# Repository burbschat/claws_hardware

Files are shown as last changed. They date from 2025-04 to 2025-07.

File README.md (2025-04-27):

# Simple SiPM/plastic scintillator based beam loss monitors
## Introduction
This repository contains the hardware design for a kind of SiPM/plastic
scintillator based beam loss monitor.
The design is based on and borrows the name (*CLAWS*) from an earlier design
employed during commissioning of the SuperKEKB collider.
A related thesis can be found [here](https://mediatum.ub.tum.de/1624845).
CLAWS was supposed to be a abbreviation for some longer name but it surely
wasn't a very elegant one, neither can I seem to remember it. Anyhow, as a
short name is quite practical, we kept on calling the system *CLAWS*.

The sensors later have been re-purposed to detect beam loss and trigger a beam
abort if there is too much of it. This application does not require very
precise sensors. Further, opposed to the original design, now a larger dynamic
range was desirable. To also allow for measurement of beam backgrounds
which occur for longer than a few microseconds, DC coupled analog electronics
are required.
The design published here was created to implement the required changes
outlined above and create a system better suited to the current application at
the SuperKEKB collider.

## Disclaimer
The circuits here have been designed by an at the time undergrad student (me)
who had no real experience in electronics or electronics CAD. I am sure there
are many aspects that I would do differently now, be it related to the circuit
itself or how it is described in KiCad.
I am however of course open for suggestions to improve the design (although I
cannot guarantee I will find the time to implement them myself).

## Overview
There are two parts to the detector system: The detectors, which are to be
placed where the beam background is expected to occur and the receiver board,
which should be placed near the digitizer, which is usually positioned outside
the radiation controlled area of the accelerator complex.

The following is an illustration of the use case at SuperKEKB (use for beam
abort), also illustrating the detector structure.
We employ a special trigger to reject short background spikes. The analog
signal however can be used in any other conceivable way depending on the exact
application.

illustration of use at SuperKEKB

### Detector Board
The detector (sometimes also referred to as the sensor) is based on a plastic
scintillator (BC-408 or similar material), light from which is detected using a
Hamamatsu SiPM (or MPPC). The SiPM is located in a small dimple in the bottom
of the scintillator. The scintillator is wrapped in an appropriately sized
reflective film (M3 DF2000MA or similar) to make sure as much as possible light
reaches the SiPM. This is the same as what was used with the earlier versions
of CLAWS and can be traced back to what is described in [this paper](https://arxiv.org/abs/1512.05900).
The wrapped scintillator is fixed to the PCB using black aluminium tape, which
also serves to shut out any light from the environment, which would overwhelm
(and potentially damage) the SiPM.

The signal obtained from the SiPM is turned into a differential signal using
the LMH6553 fully differential amplifier. The gain of this amplifier may be set
by choosing appropriate resistor values in the feedback loops of the circuit.
This amplifier then drives a differential pair in an ordinary Ethernet cable.
However, generally only CAT6A or CAT7 cables are used, as they usually provide
superior shielding, which even though a differential pair is used, appeared to
significantly lower the noise introduced by the cable.

The required voltages to drive the amplifier circuit as well as the SiPM bias
voltage are obtained from the same Ethernet cable. The amplifier here is
configured with a single 10V power supply. The voltage in the cable should be
slightly above 10V, as it is regulated by a LDO regulator on the detector
board.
10V is the maximum supply voltage supported by the LMH6553 and is chosen to
maximize the dynamic range at the amplifier output (which depends on the supply
voltage).

One twisted pair in the cable remains unused for now.

detector board V4.1

### Receiver Board
The differential signal provided by the detector board is received and properly
terminated by the receiver board. It contains a circuit using the same LMH6553
fully differential amplifier, which provides further amplification of the
received signal, as well as the option to convert it to a single ended signal.
Both inverted and non-inverted signals are supported. The not used side must be
terminated using a 50Ohm resistor (which can however also be mounted directly
on the board while leaving the corresponding output connector unpopulated).
There also is the option to further use both outputs at the same time to obtain
a differential signal.

The receiver amplifier circuit is, opposed to the one on the detector board,
arranged in a symmetric configuration. This is done to avoid a large DC bias at
the output, which poses no problem for in case of the detector board, as it is
removed by the receiver amplification circuit. The symmetric configuration
necessitates +5V and -5V supplies (for both of which there are LDO regulators
on the board).

Presumably due some unavoidable variations in the used components (resistance
values etc.), the circuit is never perfectly symmetric and thus a small DC bias
remains. The same bias appears at both outputs (inverted and non-inverted).
To compensate this, the common mode output voltage control pin of the LMH6553
is used, which is accessible through a potentiometer on the board.
As the bias is present at both outputs, one can only ever tune the circuit to
have one of them centered perfectly around zero. This however should pose no
significant problem, as in most use cases one probably only uses one of the two
outputs, or uses both to get a differential signal, for which a small DC bias
does not matter.

receiver board

The Receiver board further also distributes the voltages required by the
detector boards. These voltages as well as those needed by the receiver board
itself are supplied externally through connectors on the side of the board.
There further is the option to daisy-chain multiple receiver boards and share
the supply voltages between them. Which voltage should be connected to what is
to some degree configurable using a set of jumper pins. As regulators are used
for all but the SiPM bias voltage, the low voltages provided can be chosen
rather freely, as long as they fall within the ranges supported input of the
LDO regulators. However, testing showed that if they are on the high side, the
LDOs get rather hot. Whether this is still within the supported temperature
range was not (yet) verified.

There is also an option to use the positive voltage (before the LDO) for the
receiver board amplifier as the positive voltage for the detector board
amplifier. This turned out to be the most convenient configuration as it allows 
the setup to be powered off a +/-12V double rail supply (next to a supply for
the SiPM bias voltage).

To share voltages between receiver boards, a 10-pin ribbon cable is used. The
boards may be arranged in a stacked configuration, in case of which the
connector on the bottom must be installed and used, or a flat configuration
with a single long ribbon cable with multiple connectors.

A example for the stacked configuration is shown below. There is theoretically
also the option to add further boards of the same form factor which for example
may contain a high voltage power supply to provide the SiPM bias voltage, or
DC/DC converters to provide the other supply voltages. A mockup is shown in the
figure below.

receiver boards tower configuration

### SiPM Bias Voltage Supply
To avoid having to prepare a adjustable power supply supporting up to ~60V for
every setup, it was attempted to design a simple circuit based on the LT3571
75V DC/DC Converter for APD Bias.
The design appears to function alright, but does not provide a very flat voltage.
This to some extend is reflected in the signal form the SiPM. However, for the
application at SuperKEKB, the signal does not have to be very precise and the
introduced noise can be tolerated.

The board also does indeed emit some EMI, so care must be taken on where to
position it. There likely are possibilities to improve this design. I am open
for suggestions.

The board can be run off the same +12V as used as an input to the receiver
board. There is the option to use a DAC in combination with a microcontroller
to set the voltages and possibly read them back. I did not yet get around to
prepare a proper firmware for that. One can also simply adjust the voltage 
using a potentiometer.

There are four channels on one board, just because four of them appeared to
fit. One can just not populate the unused ones, if less than four are required.
The board does not support the same interconnect headers as the receiver boards.
This is because it mainly was designed to see if the circuit does work/is
usable at all. One could create a new version with only one channel featuring
the interconnect header.

## KiCad
The design is entirely drawn in KiCad. I like to use the newest version. The
files in this repository are for version 9.

## Libraries
There is are custom symbol and footprint library containing all the parts not
present in the standard KiCad libraries. The provided 3D models are managed
with git LFS.

## Simulation
Some of the symbols reference SPICE models in the `${KIPRJMOD}/../lib/spice_models/` directory.
Those are not present in this repository as I am probably not permitted to distribute them.
If simulation is required, please acquire the models directly from the manufacturers.

## KiBot
KiBot can be used to automate creation of gerber files, export circuit diagrams
and assembly documents or similar. The included configs are those which I used
when producing the boards at use for the SuperKEKB abort system. Adjust to taste.

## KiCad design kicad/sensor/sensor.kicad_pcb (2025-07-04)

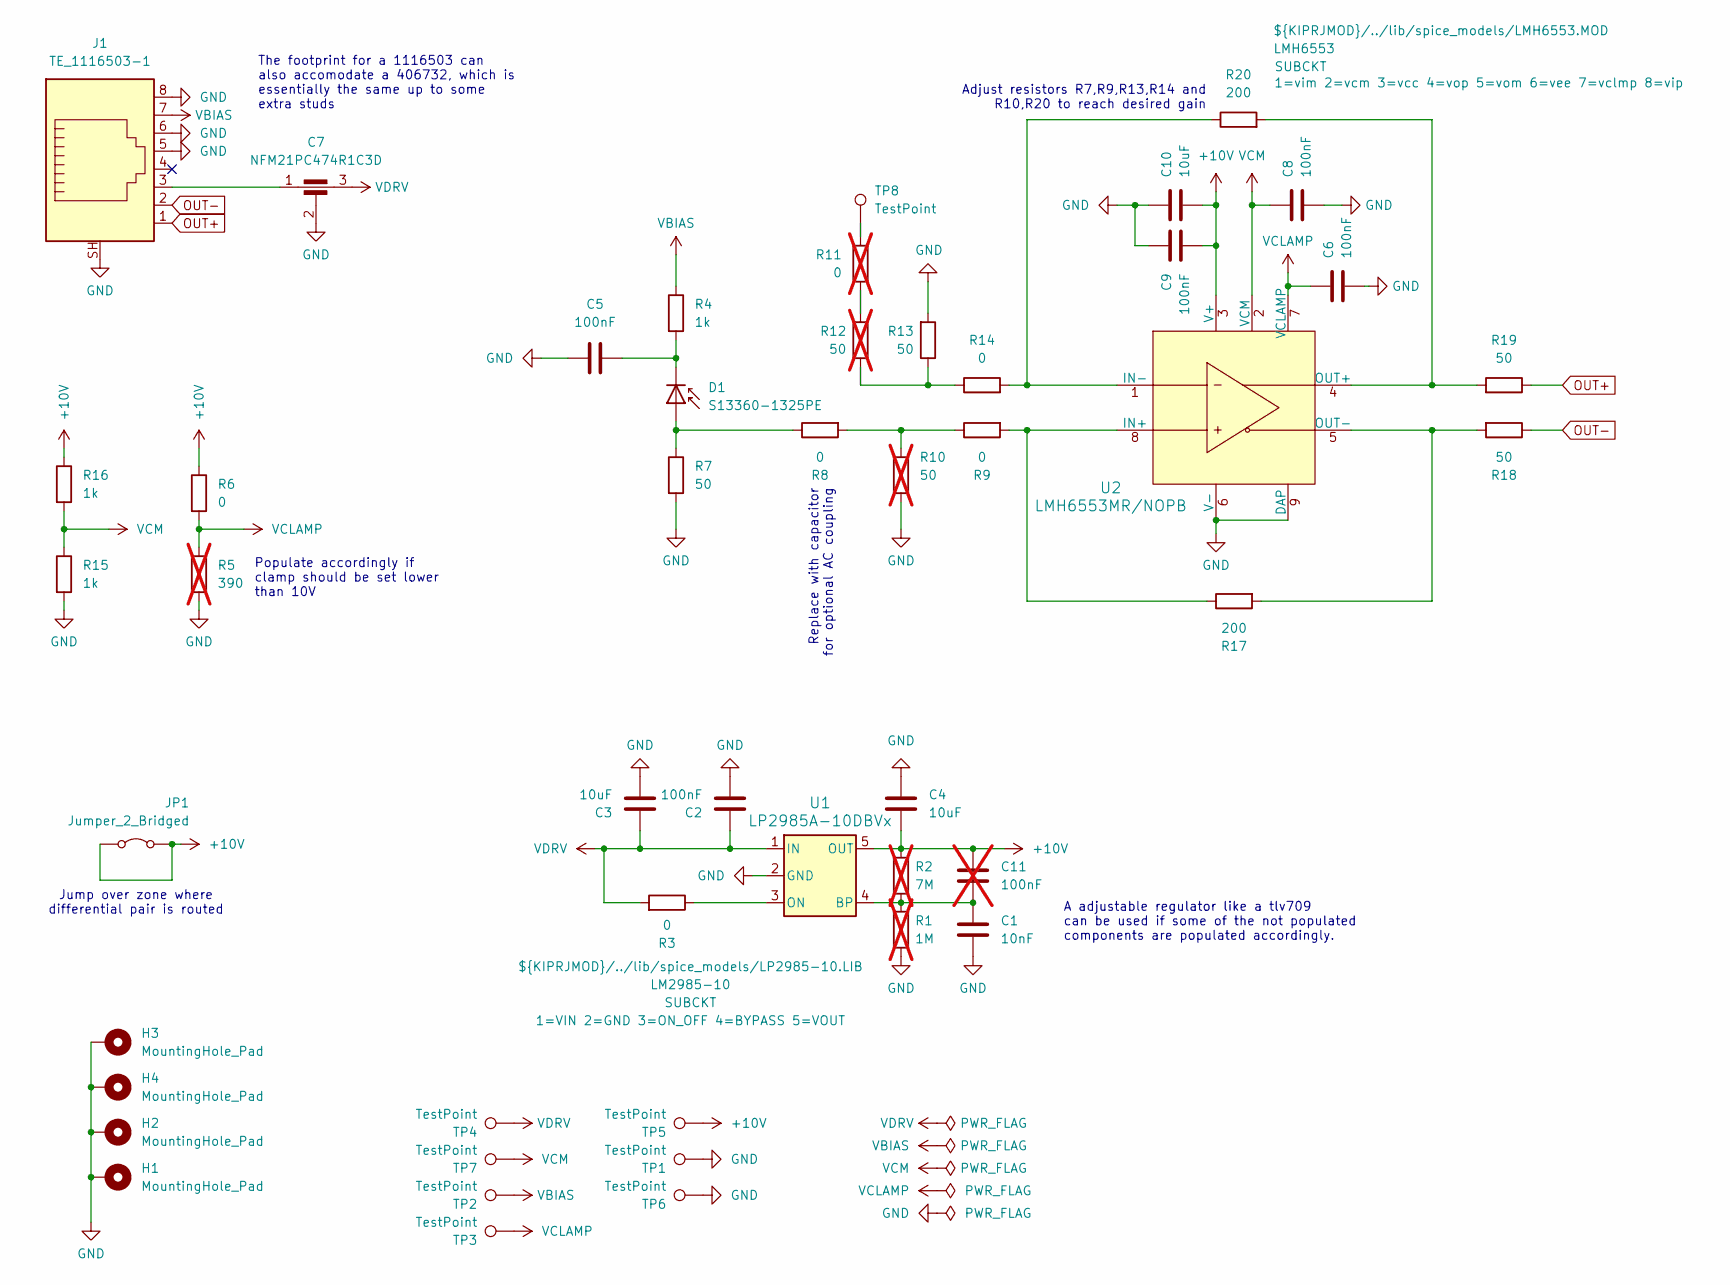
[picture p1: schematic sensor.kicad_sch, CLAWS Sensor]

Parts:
C1: 10nF; C_0603_1608Metric; Part Number GRM188R72A103KA01D
C2, C5, C6, C8, C9: 100nF; C_0603_1608Metric; Part Number GRM188R72A104KA35D
C3, C4, C10: 10uF; C_0603_1608Metric; Part Number GRM188R61E106KA73D
C7: NFM21PC474R1C3D; NFM21PC225B0J3D_MUR; Part Number NFM21PC474R1C3D
C11: 100nF; C_0603_1608Metric; Part Number GRM188R72A104KA35D; not fitted
D1: S13360-1325PE; Hamamatsu_Sxxx60-13xxXX_hand_solder; Part Number S13360-1325PE
H1, H2, H3, H4: MountingHole_Pad; MountingHole_3.2mm_M3_ISO7380_Pad_TopBottom
J1: TE_1116503-1; TE_1116503; Part Number TE_1116503-1
JP1: Jumper_2_Bridged; R_2512_6332Metric; Part Number ERJ-U1T0R00U
R1: 1M; R_0603_1608Metric; not fitted
R2: 7M; R_0603_1608Metric; not fitted
R3, R6, R8, R9, R14: 0; R_0603_1608Metric; Part Number ERJ-3GEY0R00V
R4, R15, R16: 1k; R_0603_1608Metric; Part Number ERJ-3EKF1001V
R5: 390; R_0603_1608Metric; not fitted
R7, R13, R18, R19: 50; R_0603_1608Metric; Part Number ERJ-3EKF49R9V
R10, R12: 50; R_0603_1608Metric; Part Number ERJ-3EKF49R9V; not fitted
R11: 0; R_0603_1608Metric; Part Number ERJ-3GEY0R00V; not fitted
R17, R20: 200; R_0603_1608Metric; Part Number ERJ-3GEYJ201V
TP1, TP2, TP3, TP4, TP5, TP6, TP7, TP8: TestPoint; TestPoint_THTPad_D1.5mm_Drill0.7mm
U1: LP2985A-10DBVx; SOT-23-5_DBV_TEX; Part Number LP2985A-10DBVR
U2: LMH6553MR/NOPB; MRA08B; Part Number LMH6553MRE/NOPB

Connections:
+10V: C4.1, C9.1, C10.1, C11.2, JP1.1 (A), JP1.2 (B), R2.1, R6.1, R16.1, TP5.1, U1.5 (OUT), U2.3 (V+)
GND: C1.1, C2.1, C3.1, C4.2, C5.1, C6.1, C7.2, C8.1, C9.2, C10.2, H1.1, H2.1, H3.1, H4.1, J1.5, J1.6, J1.8, J1.SH, R1.2, R5.2, R7.2, R10.2, R13.2, R15.2, TP1.1, TP6.1, U1.2 (GND), U2.6 (V-), U2.9 (DAP)
unnamed: C7.1, J1.3
unnamed: D1.3 (A), R7.1, R8.1
unnamed: C5.2, D1.2 (K), R4.2
unnamed: R8.2, R9.1, R10.1
unnamed: R11.1, TP8.1
unnamed: R11.2, R12.2
unnamed: R12.1, R13.1, R14.1
unnamed: C1.2, C11.1, R1.1, R2.2, U1.4 (BP)
unnamed: R3.1, U1.3 (ON)
unnamed: R9.2, R17.1, U2.8 (IN+)
unnamed: R14.2, R20.1, U2.1 (IN-)
unnamed: R19.2, R20.2, U2.4 (OUT+)
unnamed: R17.2, R18.2, U2.5 (OUT-)
OUT+: J1.1, R19.1
OUT-: J1.2, R18.1
VBIAS: J1.7, R4.1, TP2.1
VCLAMP: C6.2, R5.1, R6.2, TP3.1, U2.7 (VCLAMP)
VCM: C8.2, R15.1, R16.2, TP7.1, U2.2 (VCM)
VDRV: C2.2, C3.2, C7.3, R3.2, TP4.1, U1.1 (IN)

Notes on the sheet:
Adjust resistors R7,R9,R13,R14 and R10,R20 to reach desired gain
Replace with capacitor for optional AC coupling
The footprint for a 1116503 can also accomodate a 406732, which is essentially the same up to some extra studs
A adjustable regulator like a tlv709 can be used if some of the not populated components are populated accordingly.
Populate accordingly if clamp should be set lower than 10V
Jump over zone where differential pair is routed

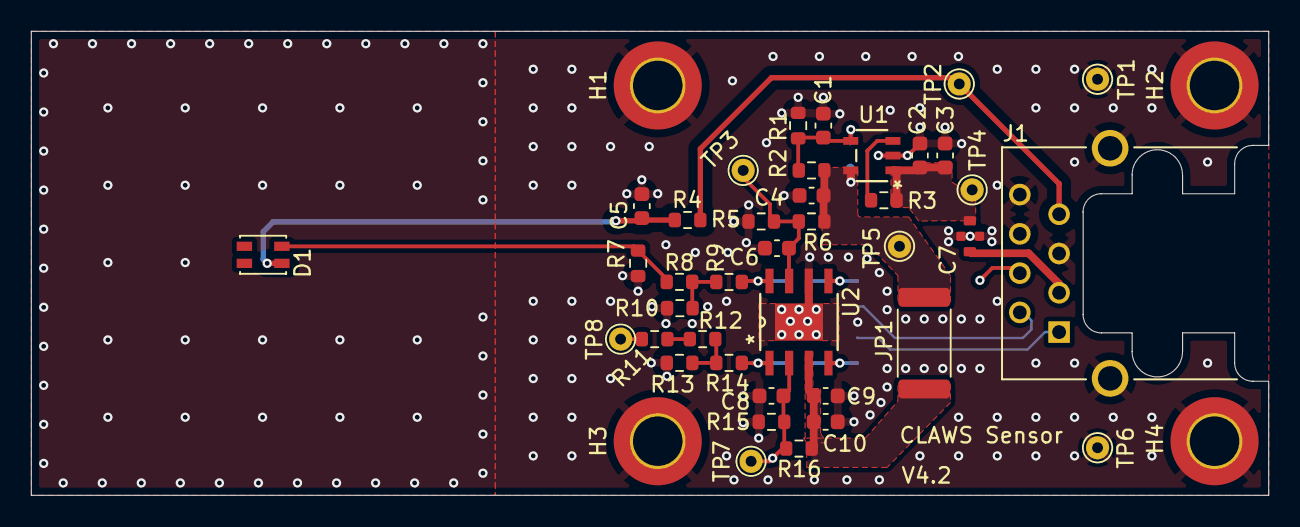
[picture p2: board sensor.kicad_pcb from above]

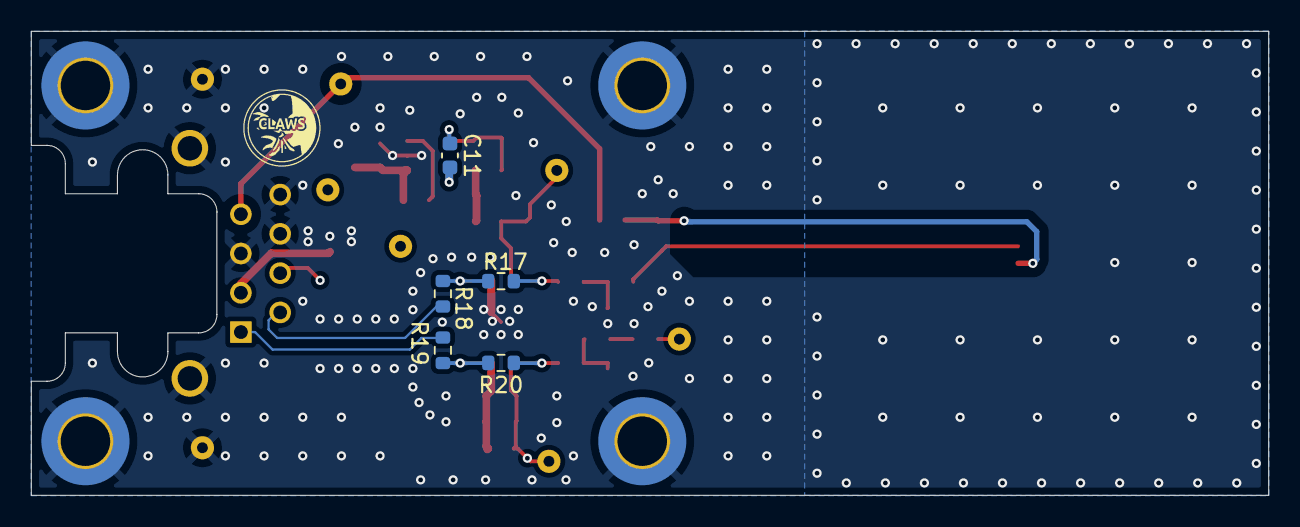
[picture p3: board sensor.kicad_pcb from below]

Board: 2 copper layers, 80.0 x 30.0 mm, 48 parts (5 on the bottom side), 21 nets.

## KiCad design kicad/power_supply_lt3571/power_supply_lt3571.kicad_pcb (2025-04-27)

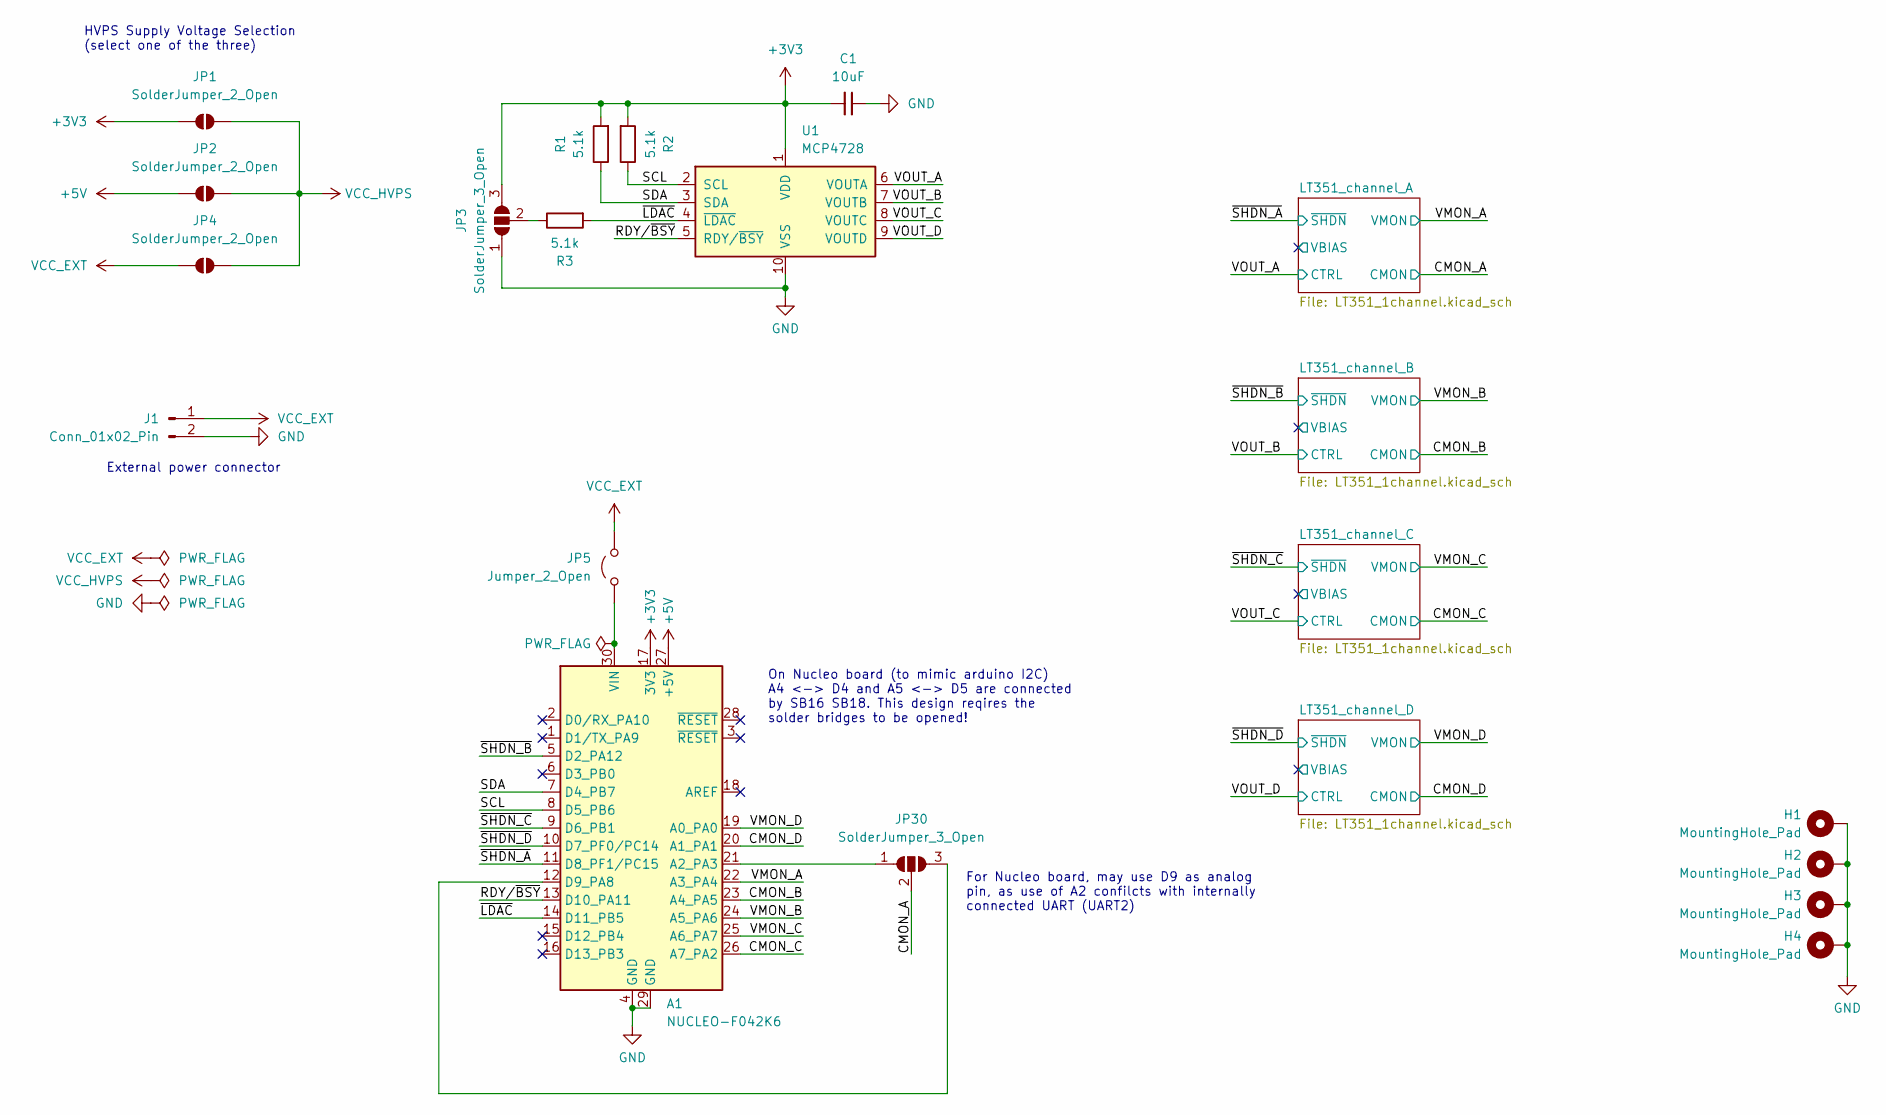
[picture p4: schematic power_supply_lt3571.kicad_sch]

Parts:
A1: NUCLEO-F042K6; NUCLEO_NANO_Hybrid
C1: 10uF; C_0603_1608Metric
H1, H2, H3, H4: MountingHole_Pad; MountingHole_3.2mm_M3_Pad_Via
J1: Conn_01x02_Pin; PhoenixContact_MCV_1,5_2-G-3.81_1x02_P3.81mm_Vertical
JP1, JP2, JP4: SolderJumper_2_Open; SolderJumper-2_P1.3mm_Open_TrianglePad1.0x1.5mm
JP3, JP30: SolderJumper_3_Open; SolderJumper-3_P2.0mm_Open_TrianglePad1.0x1.5mm_NumberLabels
JP5: Jumper_2_Open; PinHeader_1x02_P2.54mm_Vertical
R1, R2, R3: 5.1k; R_0603_1608Metric
U1: MCP4728; MSOP-10_3x3mm_P0.5mm

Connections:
+3V3: A1.17 (3V3), C1.2, JP1.1 (A), JP3.3 (B), R1.2, R2.2, U1.1 (VDD)
+5V: A1.27 (+5V), JP2.1 (A)
/CMON_A: JP30.2 (C); also elsewhere on the board
/CMON_B: A1.23 (A4_PA5); also elsewhere on the board
/CMON_C: A1.26 (A7_PA2); also elsewhere on the board
/CMON_D: A1.20 (A1_PA1); also elsewhere on the board
/RDY/~BSY: A1.13 (D10_PA11), U1.5 (RDY/~BSY)
/SCL: A1.8 (D5_PB6), R2.1, U1.2 (SCL)
/SDA: A1.7 (D4_PB7), R1.1, U1.3 (SDA)
/VMON_A: A1.22 (A3_PA4); also elsewhere on the board
/VMON_B: A1.24 (A5_PA6); also elsewhere on the board
/VMON_C: A1.25 (A6_PA7); also elsewhere on the board
/VMON_D: A1.19 (A0_PA0); also elsewhere on the board
/VOUT_A: U1.6 (VOUTA); also elsewhere on the board
/VOUT_B: U1.7 (VOUTB); also elsewhere on the board
/VOUT_C: U1.8 (VOUTC); also elsewhere on the board
/VOUT_D: U1.9 (VOUTD); also elsewhere on the board
/~LDAC: A1.14 (D11_PB5), R3.2, U1.4 (~LDAC)
/~SHDN_A: A1.11 (D8_PF1/PC15); also elsewhere on the board
/~SHDN_B: A1.5 (D2_PA12); also elsewhere on the board
/~SHDN_C: A1.9 (D6_PB1); also elsewhere on the board
/~SHDN_D: A1.10 (D7_PF0/PC14); also elsewhere on the board
GND: A1.4 (GND), A1.29 (GND), C1.1, H1.1, H2.1, H3.1, H4.1, J1.2, JP3.1 (A), U1.10 (VSS); also elsewhere on the board
unnamed: A1.21 (A2_PA3), JP30.1 (A)
unnamed: A1.12 (D9_PA8), JP30.3 (B)
unnamed: A1.30 (VIN), JP5.1 (A)
unnamed: JP3.2 (C), R3.1
VCC_EXT: J1.1, JP4.1 (A), JP5.2 (B)
VCC_HVPS: JP1.2 (B), JP2.2 (B), JP4.2 (B); also elsewhere on the board

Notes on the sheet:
On Nucleo board (to mimic arduino I2C) A4 <-> D4 and A5 <-> D5 are connected by SB16 SB18. This design reqires the solder bridges to be opened!
External power connector
HVPS Supply Voltage Selection (select one of the three)
For Nucleo board, may use D9 as analog pin, as use of A2 confilcts with internally connected UART (UART2)

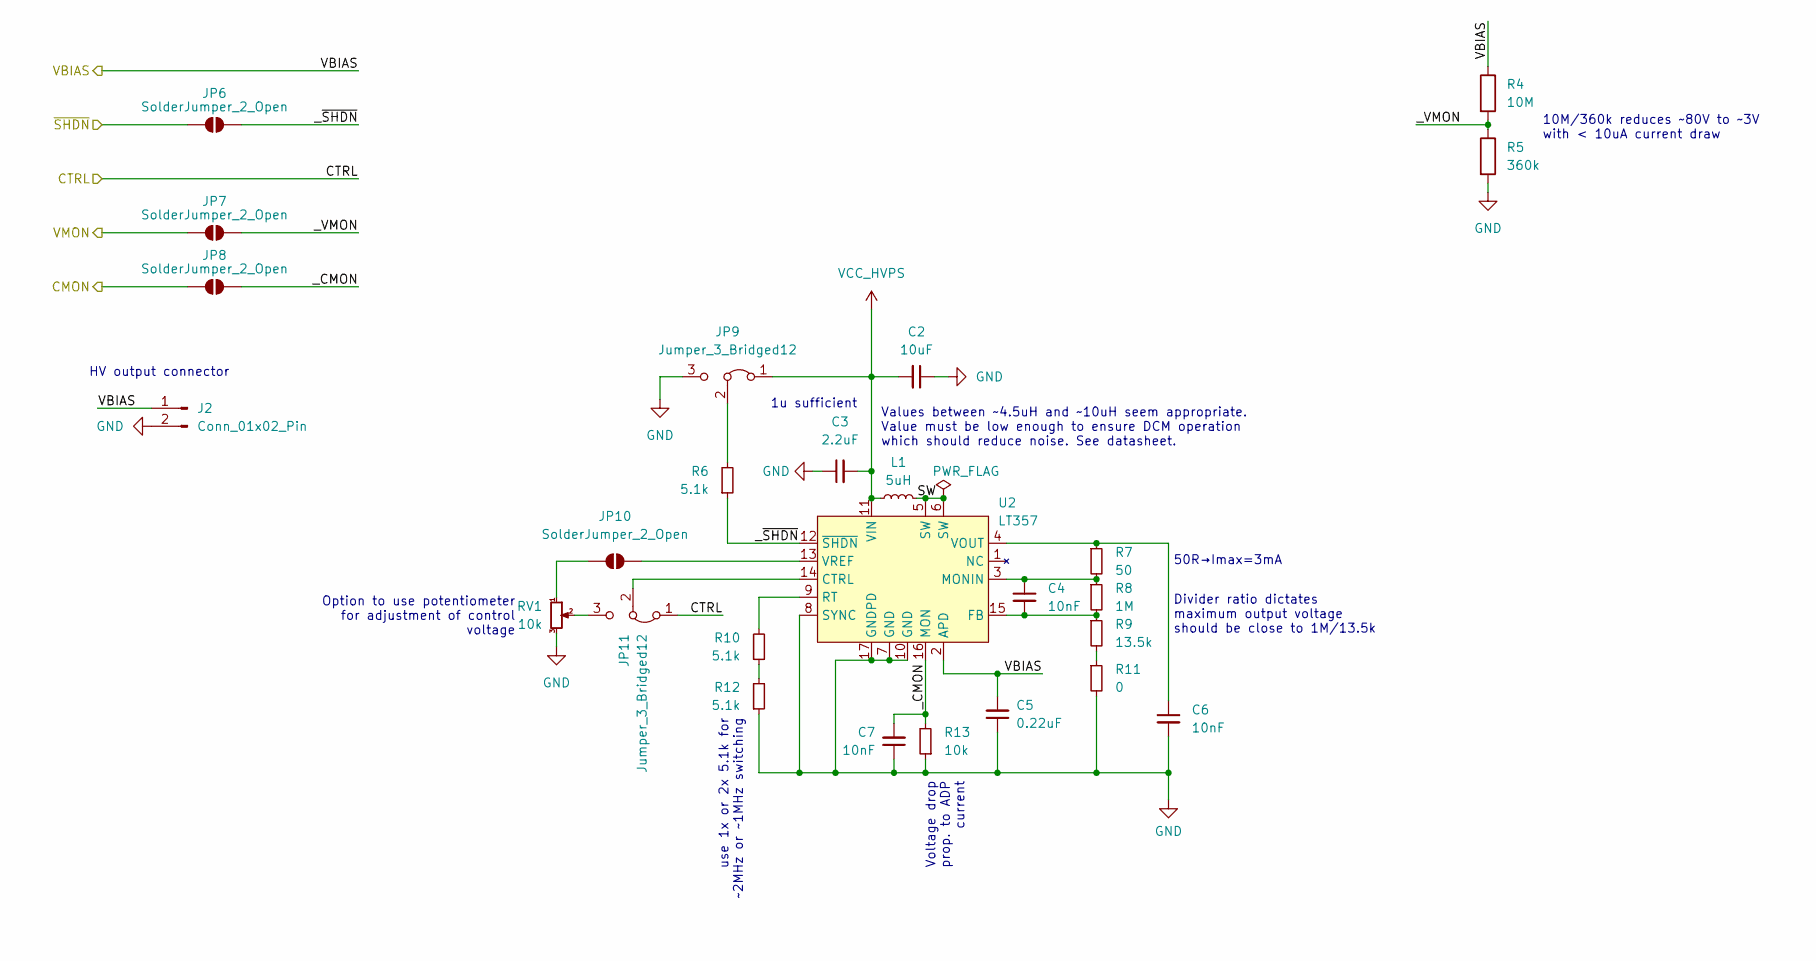
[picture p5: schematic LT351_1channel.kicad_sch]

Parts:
C2: 10uF; C_0603_1608Metric
C3: 2.2uF; C_0603_1608Metric
C4, C6, C7: 10nF; C_0603_1608Metric
C5: 0.22uF; C_1206_3216Metric
J2: Conn_01x02_Pin; PhoenixContact_MC_1,5_2-G-3.81_1x02_P3.81mm_Horizontal
JP6, JP7, JP8, JP10: SolderJumper_2_Open; SolderJumper-2_P1.3mm_Open_TrianglePad1.0x1.5mm
JP9, JP11: Jumper_3_Bridged12; PinHeader_1x03_P2.54mm_Vertical
L1: 5uH; L_1210_3225Metric
R4: 10M; R_0603_1608Metric
R5: 360k; R_0603_1608Metric
R6, R10, R12: 5.1k; R_0603_1608Metric
R7: 50; R_0603_1608Metric
R8: 1M; R_0603_1608Metric
R9: 13.5k; R_0603_1608Metric
R11: 0; R_0603_1608Metric
R13: 10k; R_0603_1608Metric
RV1: 10k; Potentiometer_Bourns_3296X_Horizontal
U2: LT357; QFN-16-1EP_3x3mm_P0.5mm_EP1.45x1.45mm_ThermalVias

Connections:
/CMON_A: JP8.1 (A); also elsewhere on the board
/LT351_channel_A/SW: L1.2, U2.5 (SW), U2.6 (SW)
/LT351_channel_A/VBIAS: C5.2, J2.1, R4.1, U2.2 (APD)
/LT351_channel_A/_CMON: C7.2, JP8.2 (B), R13.2, U2.16 (MON)
/LT351_channel_A/_VMON: JP7.2 (B), R4.2, R5.1
/LT351_channel_A/_~SHDN: JP6.2 (B), R6.1, U2.12 (~SHDN)
/VMON_A: JP7.1 (A); also elsewhere on the board
/VOUT_A: JP11.1 (A); also elsewhere on the board
/~SHDN_A: JP6.1 (A); also elsewhere on the board
GND: C2.1, C3.1, C5.1, C6.2, C7.1, J2.2, JP9.3 (B), R5.2, R11.2, R12.1, R13.1, RV1.3, U2.7 (GND), U2.8 (SYNC), U2.10 (GND), U2.17 (GNDPD); also elsewhere on the board
unnamed: JP9.2 (C), R6.2
unnamed: JP10.1 (A), RV1.1
unnamed: JP10.2 (B), U2.13 (VREF)
unnamed: JP11.3 (B), RV1.2
unnamed: JP11.2 (C), U2.14 (CTRL)
unnamed: R10.1, R12.2
unnamed: R9.2, R11.1
unnamed: C4.2, R8.2, R9.1, U2.15 (FB)
unnamed: C4.1, R7.2, R8.1, U2.3 (MONIN)
unnamed: R10.2, U2.9 (RT)
unnamed: C6.1, R7.1, U2.4 (VOUT)
VCC_HVPS: C2.2, C3.2, JP9.1 (A), L1.1, U2.11 (VIN); also elsewhere on the board

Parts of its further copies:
C8, C14, C20: 10uF; C_0603_1608Metric
C9, C15, C21: 2.2uF; C_0603_1608Metric
C10, C12, C13, C16, C18, C19, C22, C24, C25: 10nF; C_0603_1608Metric
C11, C17, C23: 0.22uF; C_1206_3216Metric
J3, J4, J5: Conn_01x02_Pin; PhoenixContact_MC_1,5_2-G-3.81_1x02_P3.81mm_Horizontal
JP12, JP13, JP14, JP16, JP18, JP19, JP20, JP22, JP24, JP25, JP26, JP28: SolderJumper_2_Open; SolderJumper-2_P1.3mm_Open_TrianglePad1.0x1.5mm
JP15, JP17, JP21, JP23, JP27, JP29: Jumper_3_Bridged12; PinHeader_1x03_P2.54mm_Vertical
L2, L3, L4: 5uH; L_1210_3225Metric
R14, R24, R34: 10M; R_0603_1608Metric
R15, R25, R35: 360k; R_0603_1608Metric
R16, R20, R22, R26, R30, R32, R36, R40, R42: 5.1k; R_0603_1608Metric
R17, R27, R37: 50; R_0603_1608Metric
R18, R28, R38: 1M; R_0603_1608Metric
R19, R29, R39: 13.5k; R_0603_1608Metric
R21, R31, R41: 0; R_0603_1608Metric
R23, R33, R43: 10k; R_0603_1608Metric
RV2, RV3, RV4: 10k; Potentiometer_Bourns_3296X_Horizontal
U3, U4, U5: LT357; QFN-16-1EP_3x3mm_P0.5mm_EP1.45x1.45mm_ThermalVias

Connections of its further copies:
/CMON_B: JP14.1 (A); also elsewhere on the board
/CMON_C: JP20.1 (A); also elsewhere on the board
/CMON_D: JP26.1 (A); also elsewhere on the board
/LT351_channel_B/SW: L2.2, U3.5 (SW), U3.6 (SW)
/LT351_channel_B/VBIAS: C11.2, J3.1, R14.1, U3.2 (APD)
/LT351_channel_B/_CMON: C13.2, JP14.2 (B), R23.2, U3.16 (MON)
/LT351_channel_B/_VMON: JP13.2 (B), R14.2, R15.1
/LT351_channel_B/_~SHDN: JP12.2 (B), R16.1, U3.12 (~SHDN)
/LT351_channel_C/SW: L3.2, U4.5 (SW), U4.6 (SW)
/LT351_channel_C/VBIAS: C17.2, J4.1, R24.1, U4.2 (APD)
/LT351_channel_C/_CMON: C19.2, JP20.2 (B), R33.2, U4.16 (MON)
/LT351_channel_C/_VMON: JP19.2 (B), R24.2, R25.1
/LT351_channel_C/_~SHDN: JP18.2 (B), R26.1, U4.12 (~SHDN)
/LT351_channel_D/SW: L4.2, U5.5 (SW), U5.6 (SW)
/LT351_channel_D/VBIAS: C23.2, J5.1, R34.1, U5.2 (APD)
/LT351_channel_D/_CMON: C25.2, JP26.2 (B), R43.2, U5.16 (MON)
/LT351_channel_D/_VMON: JP25.2 (B), R34.2, R35.1
/LT351_channel_D/_~SHDN: JP24.2 (B), R36.1, U5.12 (~SHDN)
/VMON_B: JP13.1 (A); also elsewhere on the board
/VMON_C: JP19.1 (A); also elsewhere on the board
/VMON_D: JP25.1 (A); also elsewhere on the board
/VOUT_B: JP17.1 (A); also elsewhere on the board
/VOUT_C: JP23.1 (A); also elsewhere on the board
/VOUT_D: JP29.1 (A); also elsewhere on the board
/~SHDN_B: JP12.1 (A); also elsewhere on the board
/~SHDN_C: JP18.1 (A); also elsewhere on the board
/~SHDN_D: JP24.1 (A); also elsewhere on the board
GND: C8.1, C9.1, C11.1, C12.2, C13.1, C14.1, C15.1, C17.1, C18.2, C19.1, C20.1, C21.1, C23.1, C24.2, C25.1, J3.2, J4.2, J5.2, JP15.3 (B), JP21.3 (B), JP27.3 (B), R15.2, R21.2, R22.1, R23.1, R25.2, R31.2, R32.1, R33.1, R35.2, R41.2, R42.1, R43.1, RV2.3, RV3.3, RV4.3, U3.7 (GND), U3.8 (SYNC), U3.10 (GND), U3.17 (GNDPD), U4.7 (GND), U4.8 (SYNC), U4.10 (GND), U4.17 (GNDPD), U5.7 (GND), U5.8 (SYNC), U5.10 (GND), U5.17 (GNDPD); also elsewhere on the board
unnamed: JP15.2 (C), R16.2
unnamed: JP16.1 (A), RV2.1
unnamed: JP16.2 (B), U3.13 (VREF)
unnamed: JP17.3 (B), RV2.2
unnamed: JP17.2 (C), U3.14 (CTRL)
unnamed: JP21.2 (C), R26.2
unnamed: JP22.1 (A), RV3.1
unnamed: JP22.2 (B), U4.13 (VREF)
unnamed: JP23.3 (B), RV3.2
unnamed: JP23.2 (C), U4.14 (CTRL)
unnamed: JP27.2 (C), R36.2
unnamed: JP28.1 (A), RV4.1
unnamed: JP28.2 (B), U5.13 (VREF)
unnamed: JP29.3 (B), RV4.2
unnamed: JP29.2 (C), U5.14 (CTRL)
unnamed: R19.2, R21.1
unnamed: R20.1, R22.2
unnamed: R29.2, R31.1
unnamed: R30.1, R32.2
unnamed: R39.2, R41.1
unnamed: R40.1, R42.2
unnamed: C10.2, R18.2, R19.1, U3.15 (FB)
unnamed: C10.1, R17.2, R18.1, U3.3 (MONIN)
unnamed: R20.2, U3.9 (RT)
unnamed: C12.1, R17.1, U3.4 (VOUT)
unnamed: C16.2, R28.2, R29.1, U4.15 (FB)
unnamed: C16.1, R27.2, R28.1, U4.3 (MONIN)
unnamed: R30.2, U4.9 (RT)
unnamed: C18.1, R27.1, U4.4 (VOUT)
unnamed: C22.2, R38.2, R39.1, U5.15 (FB)
unnamed: C22.1, R37.2, R38.1, U5.3 (MONIN)
unnamed: R40.2, U5.9 (RT)
unnamed: C24.1, R37.1, U5.4 (VOUT)
VCC_HVPS: C8.2, C9.2, C14.2, C15.2, C20.2, C21.2, JP15.1 (A), JP21.1 (A), JP27.1 (A), L2.1, L3.1, L4.1, U3.11 (VIN), U4.11 (VIN), U5.11 (VIN); also elsewhere on the board

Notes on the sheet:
HV output connector
50R→Imax=3mA
use 1x or 2x 5.1k for ~2MHz or ~1MHz switching
10M/360k reduces ~80V to ~3V with < 10uA current draw
Values between ~4.5uH and ~10uH seem appropriate. Value must be low enough to ensure DCM operation which should reduce noise. See datasheet.
1u sufficient
Divider ratio dictates maximum output voltage should be close to 1M/13.5k
Option to use potentiometer for adjustment of control voltage
Voltage drop prop. to ADP current

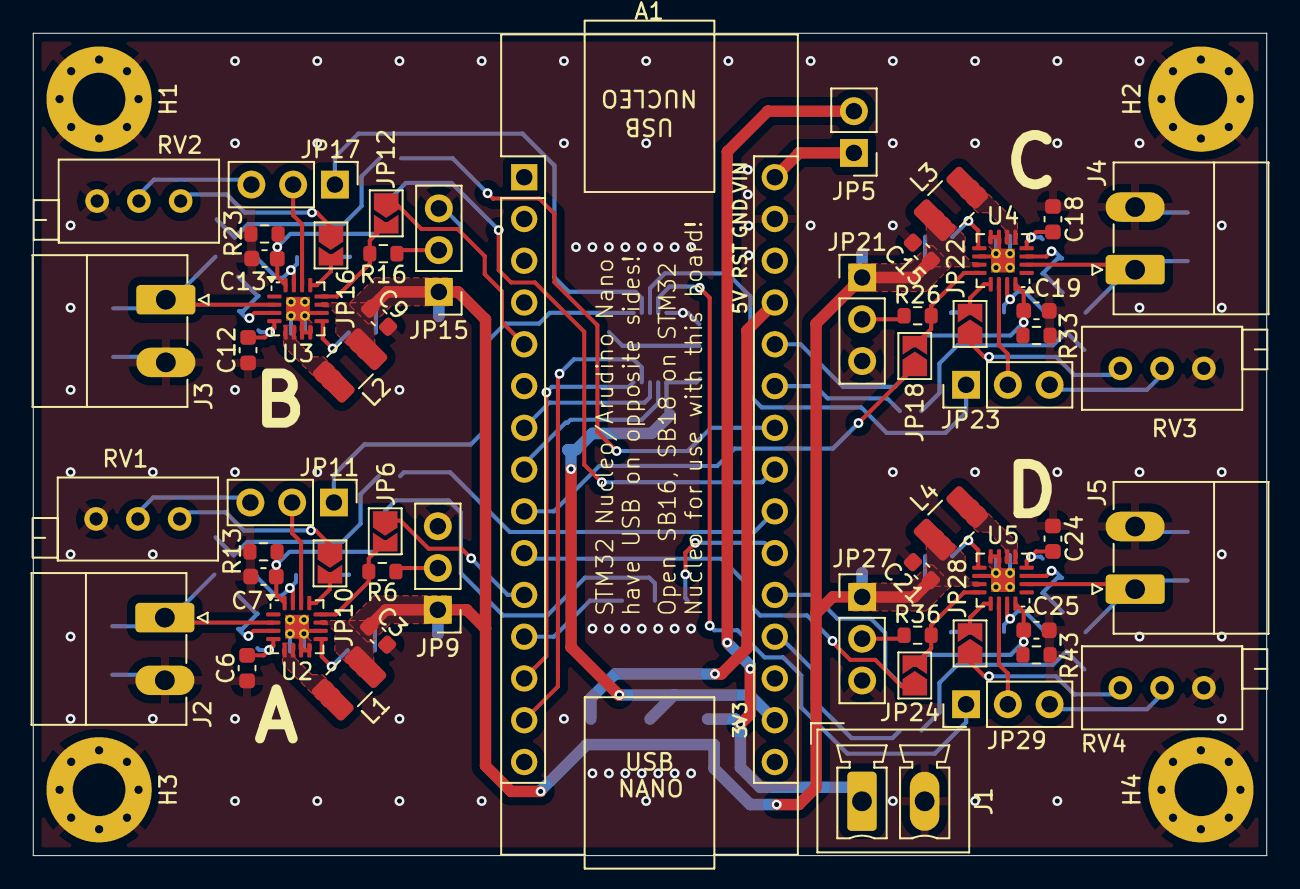
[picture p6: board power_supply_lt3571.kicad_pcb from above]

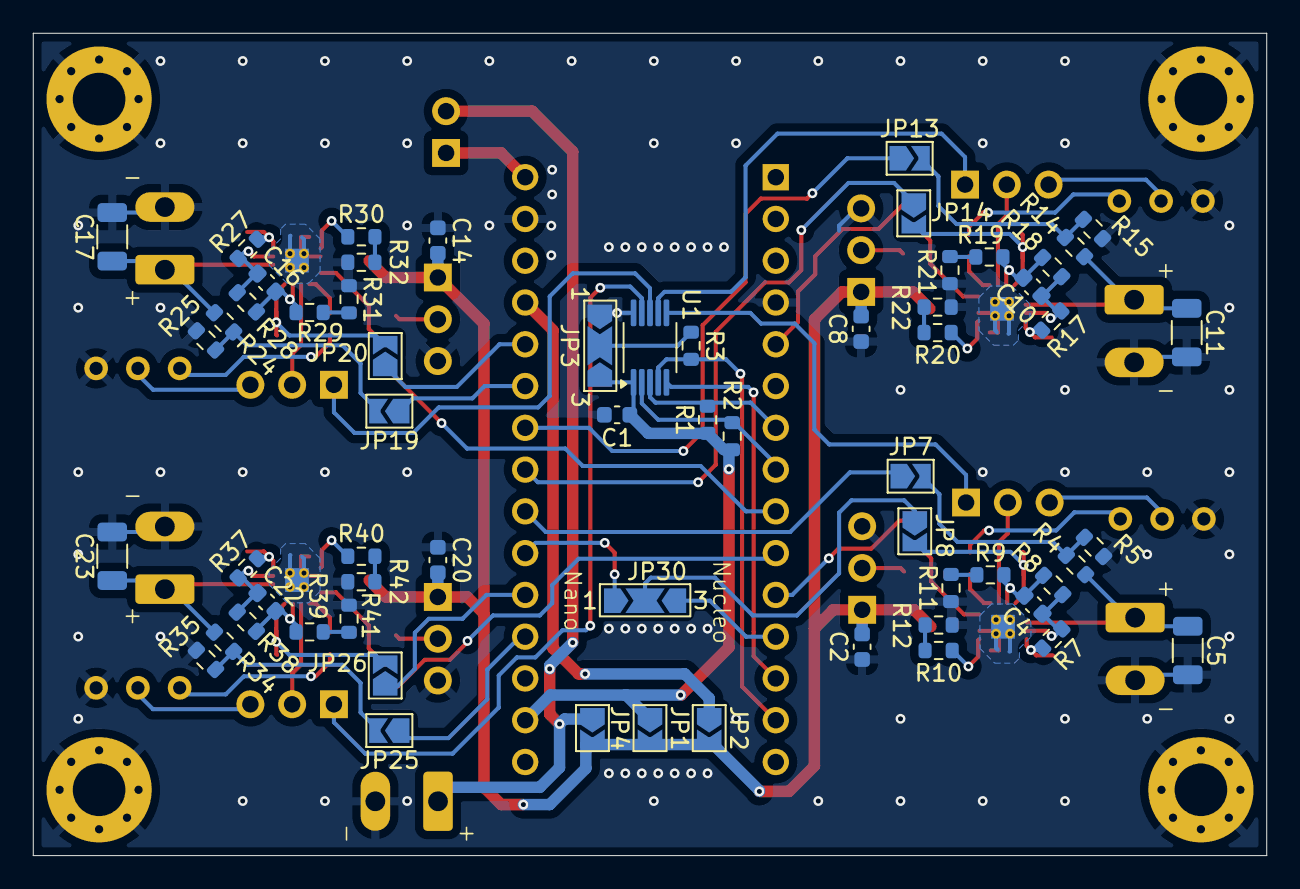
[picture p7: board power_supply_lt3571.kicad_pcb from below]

Board: 2 copper layers, 75.0 x 50.0 mm, 121 parts (62 on the bottom side), 93 nets.

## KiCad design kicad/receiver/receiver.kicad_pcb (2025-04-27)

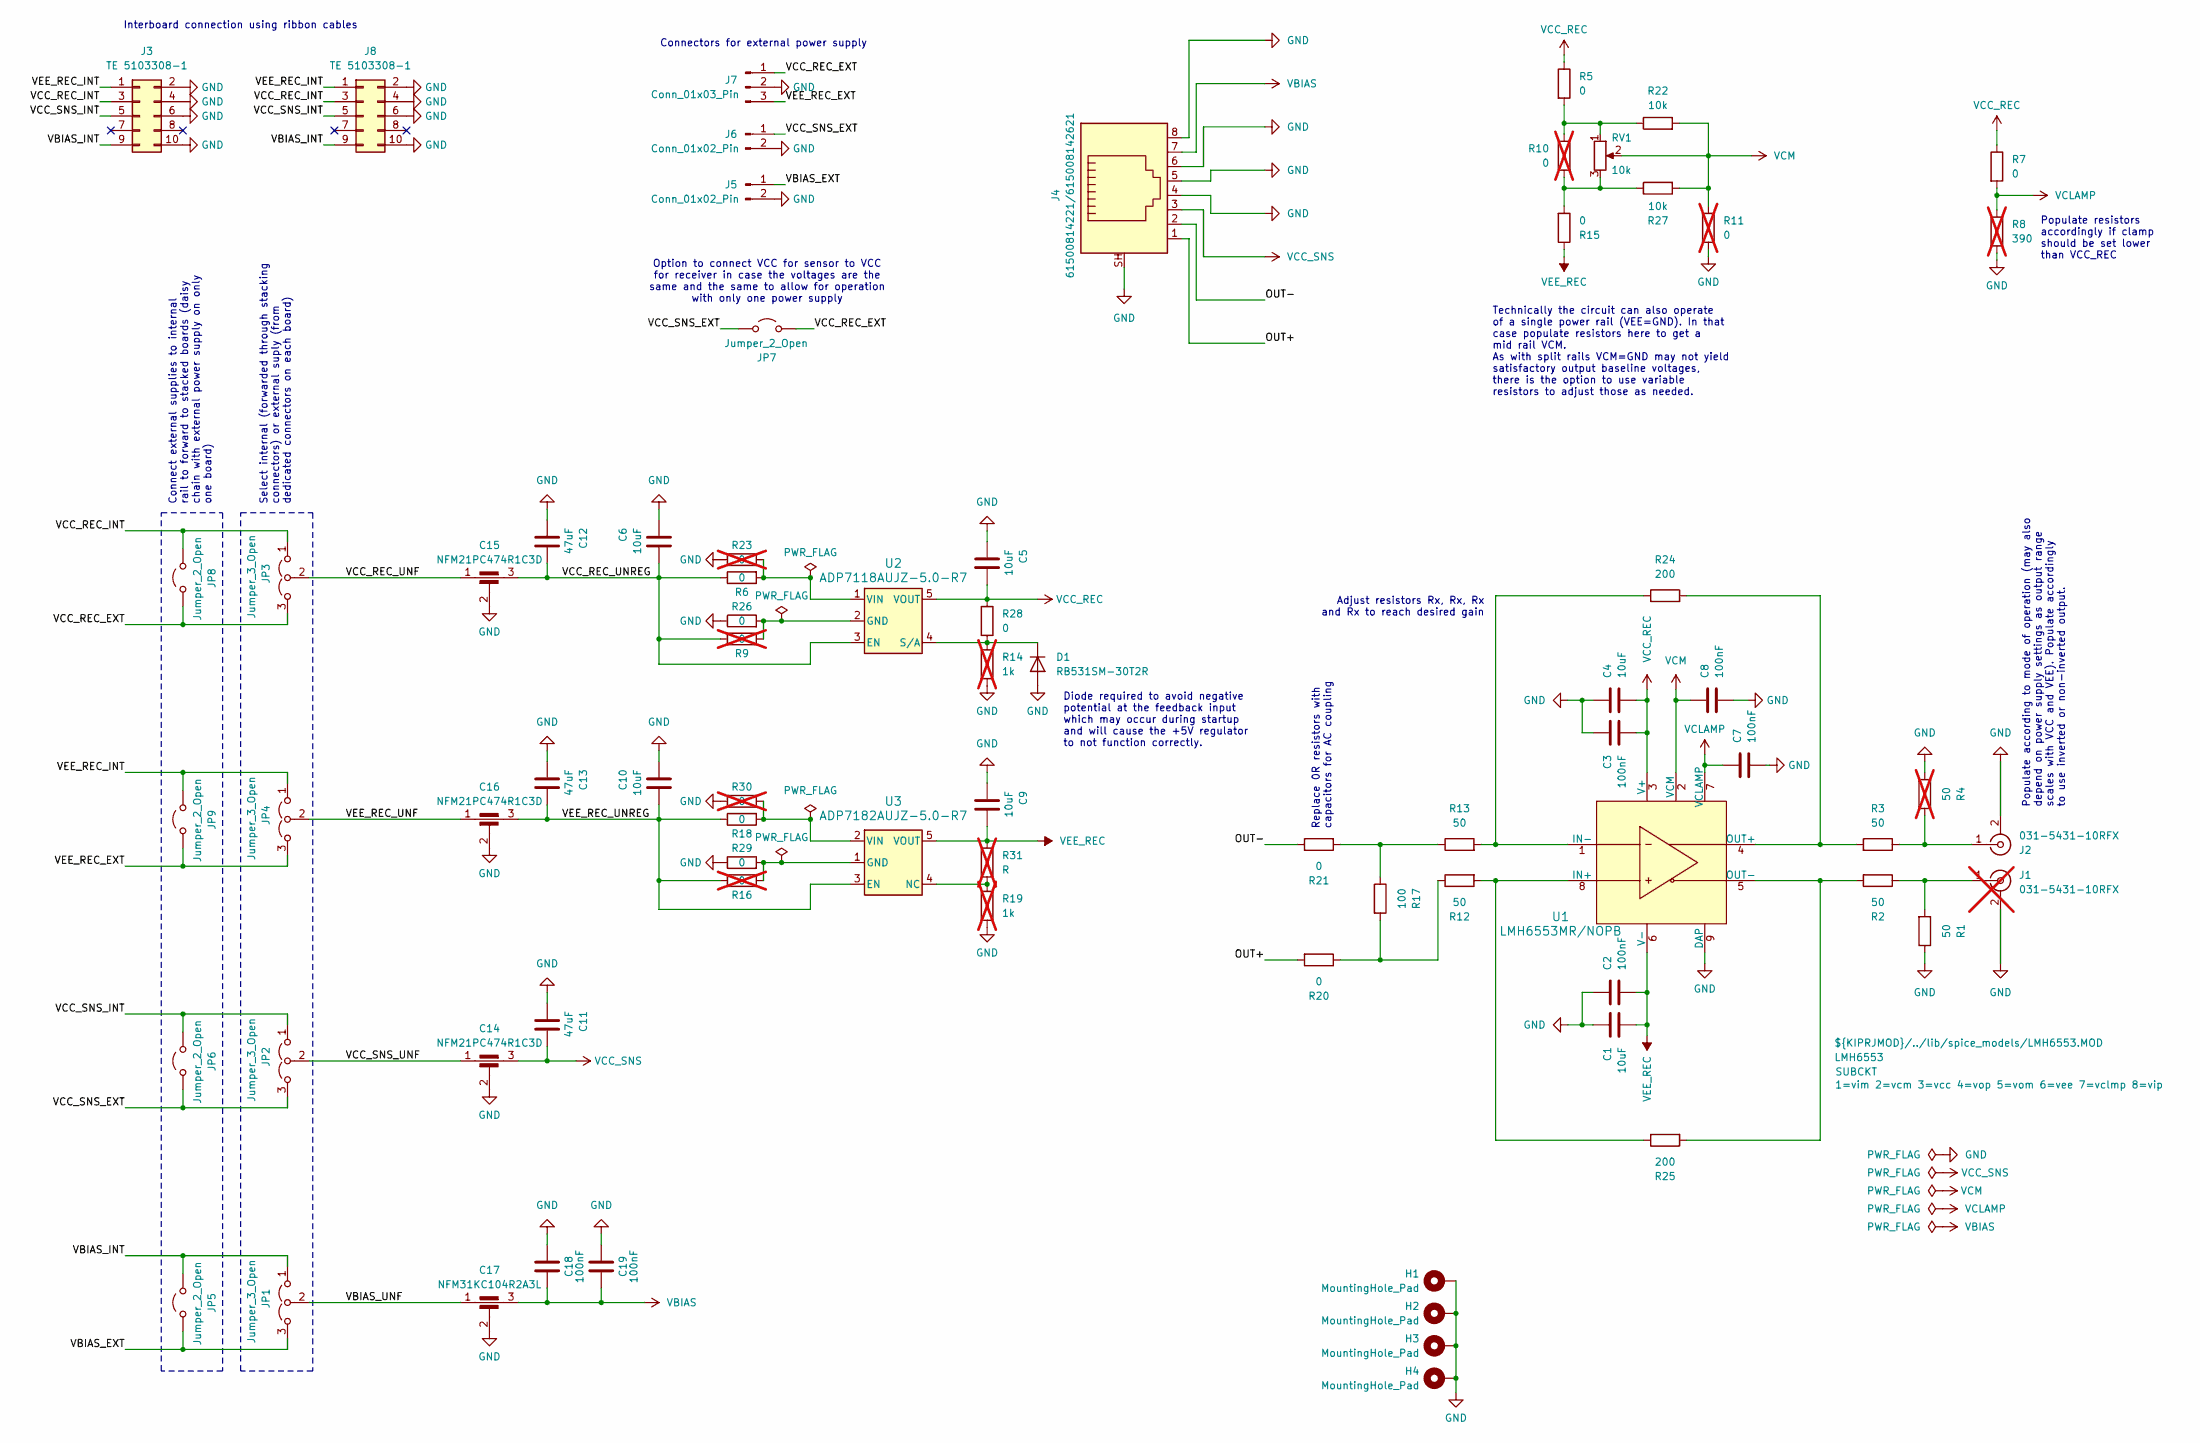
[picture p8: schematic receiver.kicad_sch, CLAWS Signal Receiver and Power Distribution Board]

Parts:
C1, C4, C5, C6, C9, C10: 10uF; C_0603_1608Metric; Part Number GRM188R61E106KA73D
C2, C3, C7, C8, C18, C19: 100nF; C_0603_1608Metric; Part Number GRM188R72A104KA35D
C11, C12, C13: 47uF; C_1210_3225Metric; Part Number GRM32EC81C476KE15K
C14, C15, C16: NFM21PC474R1C3D; NFM21PC225B0J3D_MUR; Part Number NFM21PC474R1C3D
C17: NFM31KC104R2A3L; NFM31KC104R2A3_MUR; Part Number NFM31KC104R2A3L
D1: RB531SM-30T2R; D_SOD-523; Part Number RB531SM-30T2R
H1, H2, H3, H4: MountingHole_Pad; MountingHole_3.2mm_M3_Pad_Via
J1: 031-5431-10RFX; BNC_Amphenol_031-5431-10RFX_Horizontal; Part Number 031-5431-10RFX; not fitted
J2: 031-5431-10RFX; BNC_Amphenol_031-5431-10RFX_Horizontal; Part Number 031-5431-10RFX
J3, J8: TE 5103308-1; PinHeader_2x05_P2.54mm_Vertical_Ribbon; Part Number 5103308-1
J4: 61500814221/615008142621; 61500814221_615008142621_hybrid; Part Number 61500814221
J5, J6: Conn_01x02_Pin; PhoenixContact_MC_1,5_2-G-3.81_1x02_P3.81mm_Horizontal; Part Number 1803277
J7: Conn_01x03_Pin; PhoenixContact_MC_1,5_3-G-3.81_1x03_P3.81mm_Horizontal; Part Number 1803280
JP1, JP2, JP3, JP4: Jumper_3_Open; PinHeader_1x03_P2.54mm_Vertical
JP5, JP6, JP7, JP8, JP9: Jumper_2_Open; PinHeader_1x02_P2.54mm_Vertical
R1, R2, R3, R12, R13: 50; R_0603_1608Metric; Part Number ERJ-3EKF49R9V
R4: 50; R_0603_1608Metric; Part Number ERJ-3EKF49R9V; not fitted
R5, R6, R7, R15, R18, R20, R21, R26, R28, R29: 0; R_0603_1608Metric; Part Number ERJ-3GEY0R00V
R8: 390; R_0603_1608Metric; not fitted
R9, R10, R11, R16, R23, R30: 0; R_0603_1608Metric; Part Number ERJ-3GEY0R00V; not fitted
R14, R19: 1k; R_0603_1608Metric; Part Number ERJ-3EKF1001V; not fitted
R17: 100; R_0603_1608Metric; Part Number ERJ-3EKF1000V
R22, R27: 10k; R_0603_1608Metric; Part Number ERJ-3EKF1002V
R24, R25: 200; R_0603_1608Metric; Part Number ERJ-3GEYJ201V
R31: R; R_0603_1608Metric; not fitted
RV1: 10k; Potentiometer_Bourns_3296X_Horizontal; Part Number 3296X-1-103LF
U1: LMH6553MR/NOPB; MRA08B; Part Number LMH6553MRE/NOPB
U2: ADP7118AUJZ-5.0-R7; TSOT-23-5; Part Number ADP7118AUJZ-5.0-R7
U3: ADP7182AUJZ-5.0-R7; TSOT-23-5; Part Number ADP7182AUJZ-5.0-R7

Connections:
/OUT+: J4.1, R20.2
/OUT-: J4.2, R21.1
/VBIAS_EXT: J5.1, JP1.3 (B), JP5.2 (B)
/VBIAS_INT: J3.9, J8.9, JP1.1 (A), JP5.1 (A)
/VBIAS_UNF: C17.1, JP1.2 (C)
/VCC_REC_EXT: J7.1, JP3.3 (B), JP7.1 (A), JP8.2 (B)
/VCC_REC_INT: J3.3, J8.3, JP3.1 (A), JP8.1 (A)
/VCC_REC_UNF: C15.1, JP3.2 (C)
/VCC_REC_UNREG: C6.1, C12.1, C15.3, R6.1, R9.1, U2.3 (EN)
/VCC_SNS_EXT: J6.1, JP2.3 (B), JP6.2 (B), JP7.2 (B)
/VCC_SNS_INT: J3.5, J8.5, JP2.1 (A), JP6.1 (A)
/VCC_SNS_UNF: C14.1, JP2.2 (C)
/VEE_REC_EXT: J7.3, JP4.3 (B), JP9.2 (B)
/VEE_REC_INT: J3.1, J8.1, JP4.1 (A), JP9.1 (A)
/VEE_REC_UNF: C16.1, JP4.2 (C)
/VEE_REC_UNREG: C10.1, C13.1, C16.3, R16.1, R18.1, U3.3 (EN)
GND: C1.2, C2.2, C3.2, C4.2, C5.2, C6.2, C7.1, C8.1, C9.2, C10.2, C11.2, C12.2, C13.2, C14.2, C15.2, C16.2, C17.2, C18.1, C19.1, D1.2 (A), H1.1, H2.1, H3.1, H4.1, J1.2 (Ext), J2.2 (Ext), J3.2, J3.4, J3.6, J3.10, J4.4, J4.5, J4.6, J4.8, J4.SH, J5.2, J6.2, J7.2, J8.2, J8.4, J8.6, J8.10, R1.1, R4.1, R8.2, R11.2, R14.2, R19.2, R23.1, R26.1, R29.1, R30.1, U1.9 (DAP)
unnamed: D1.1 (K), R14.1, R28.2, U2.4 (S/A)
unnamed: J1.1 (In), R1.2, R2.1
unnamed: J2.1 (In), R3.1, R4.2
unnamed: R5.2, R10.1, R22.1, RV1.1
unnamed: R10.2, R15.2, R27.1, RV1.3
unnamed: R12.1, R17.2, R20.1
unnamed: R13.1, R17.1, R21.2
unnamed: R12.2, R25.1, U1.8 (IN+)
unnamed: R13.2, R24.1, U1.1 (IN-)
unnamed: R3.2, R24.2, U1.4 (OUT+)
unnamed: R2.2, R25.2, U1.5 (OUT-)
unnamed: R9.2, R26.2, U2.2 (GND)
unnamed: R6.2, R23.2, U2.1 (VIN)
unnamed: R16.2, R29.2, U3.1 (GND)
unnamed: R19.1, R31.2, U3.4 (NC)
unnamed: R18.2, R30.2, U3.2 (VIN)
VBIAS: C17.3, C18.2, C19.2, J4.7
VCC_REC: C3.1, C4.1, C5.1, R5.1, R7.1, R28.1, U1.3 (V+), U2.5 (VOUT)
VCC_SNS: C11.1, C14.3, J4.3
VCLAMP: C7.2, R7.2, R8.1, U1.7 (VCLAMP)
VCM: C8.2, R11.1, R22.2, R27.2, RV1.2, U1.2 (VCM)
VEE_REC: C1.1, C2.1, C9.1, R15.1, R31.1, U1.6 (V-), U3.5 (VOUT)

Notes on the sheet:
Connect external supplies to internal rail to forward to stacked boards (daisy chain with external power supply on only one board)
Interboard connection using ribbon cables
Populate resistors accordingly if clamp should be set lower than VCC_REC
Select internal (forwarded through stacking connectors) or external suply (from dedicated connectors on each board)
Populate according to mode of operation (may also depend on power supply settings as output range scales with VCC and VEE). Populate accordingly to use inverted or non-inverted output.
Replace 0R resistors with capacitors for AC coupling
Technically the circuit can also operate of a single power rail (VEE=GND). In that case populate resistors here to get a mid rail VCM. As with split rails VCM=GND may not yield satisfactory output baseline voltages, there is the option to use variable resistors to adjust those as needed.
Connectors for external power supply
Diode required to avoid negative potential at the feedback input which may occur during startup and will cause the +5V regulator to not function correctly.
Adjust resistors Rx, Rx, Rx and Rx to reach desired gain
Option to connect VCC for sensor to VCC for receiver in case the voltages are the same and the same to allow for operation with only one power supply

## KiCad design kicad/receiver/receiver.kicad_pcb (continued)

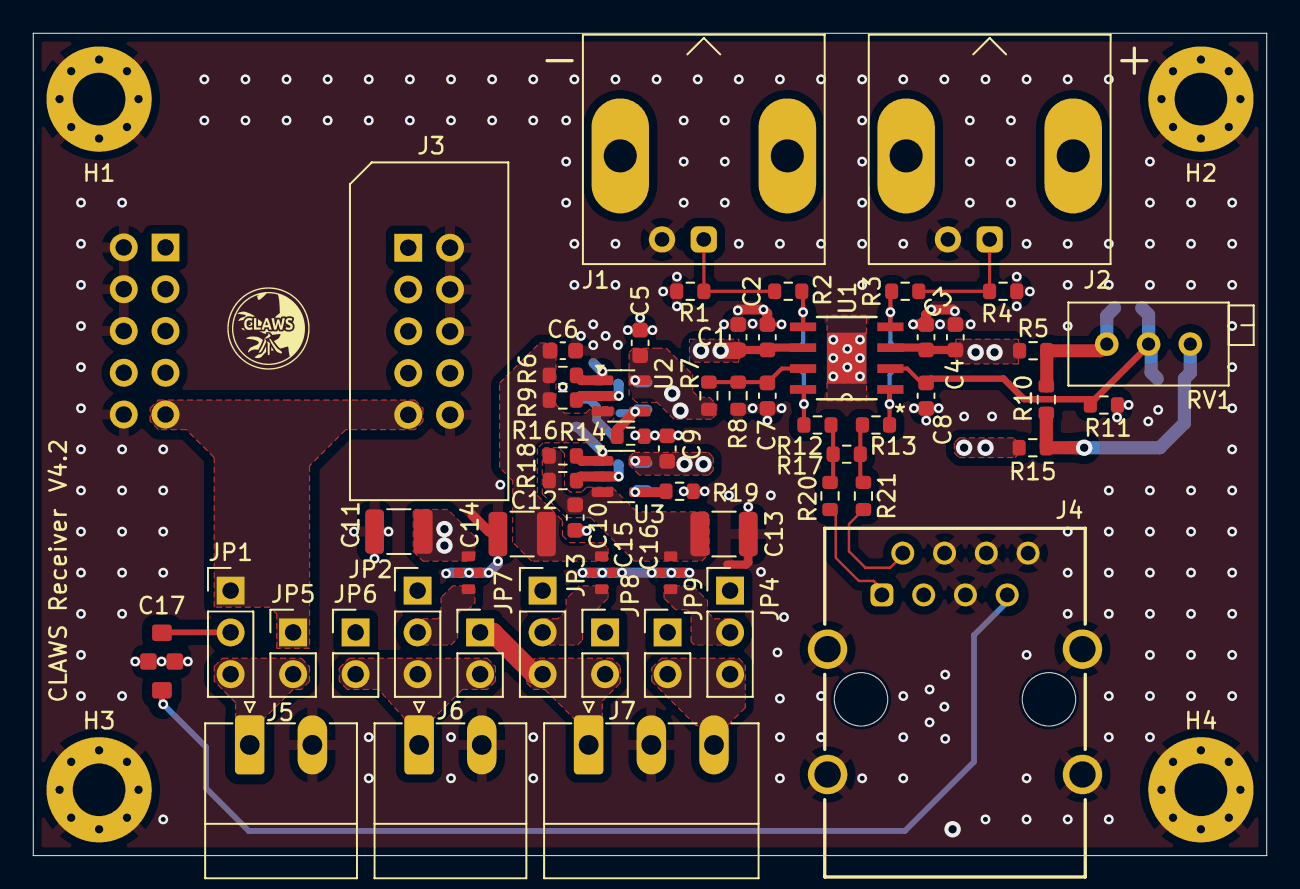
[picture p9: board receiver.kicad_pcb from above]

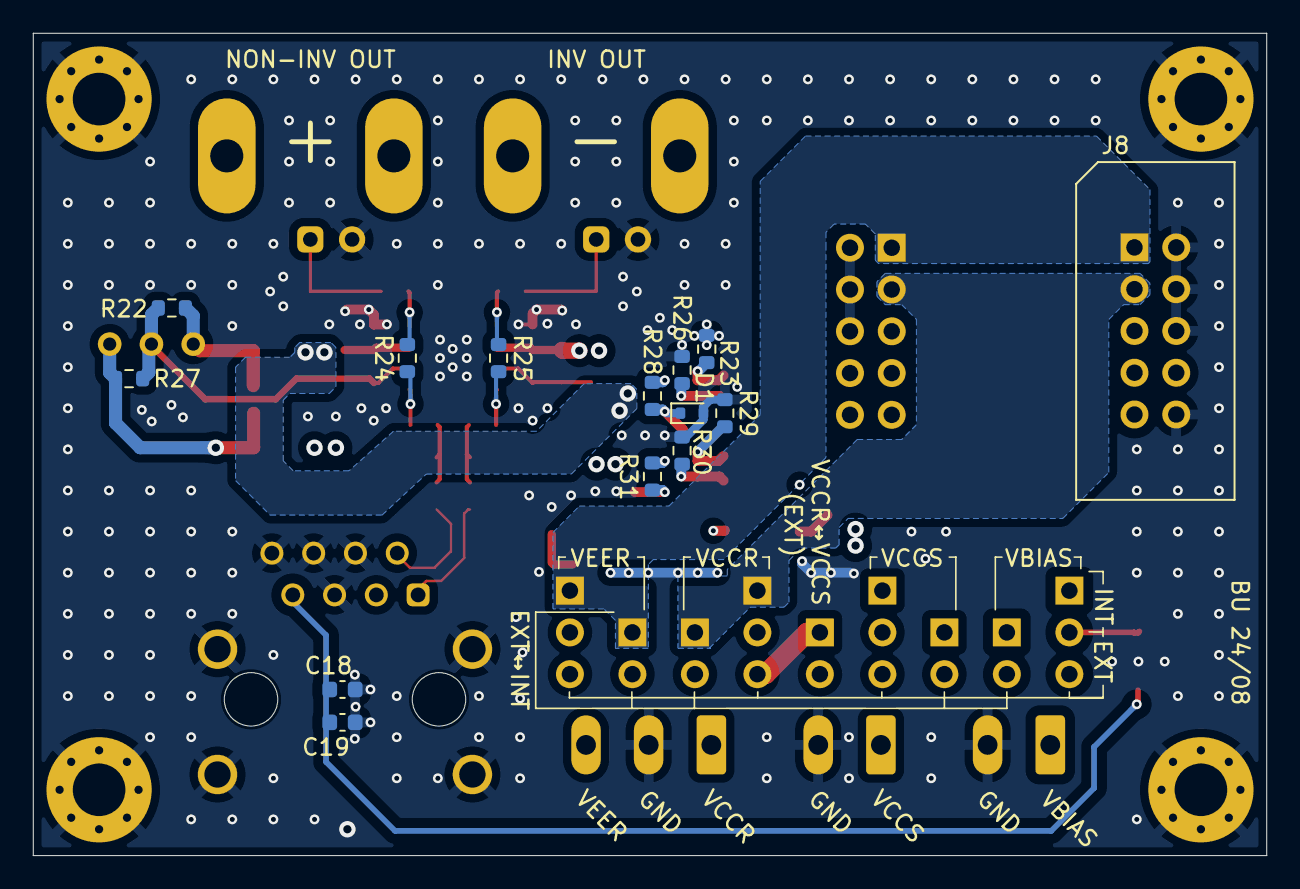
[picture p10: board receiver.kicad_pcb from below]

Board: 4 copper layers, 75.0 x 50.0 mm, 76 parts (14 on the bottom side), 39 nets.

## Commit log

2025-04-27 Add KiCad project for sensor
    [sensor.kicad_pcb, sensor.kicad_sch]
2025-04-27 Add KiCad project for receiver
    [receiver.kicad_pcb, receiver.kicad_sch]
2025-04-27 Add KiCad project for SiPM power supply
    Or a voltage supply if you prefer. It does not really provide much
    'power'.
    [LT351_1channel.kicad_sch, power_supply_lt3571.kicad_pcb, power_supply_lt3571.kicad_sch]
2025-07-04 Properly exclude tolerated DRC errors and fix silkscreen overlap
    [sensor.kicad_pcb]
